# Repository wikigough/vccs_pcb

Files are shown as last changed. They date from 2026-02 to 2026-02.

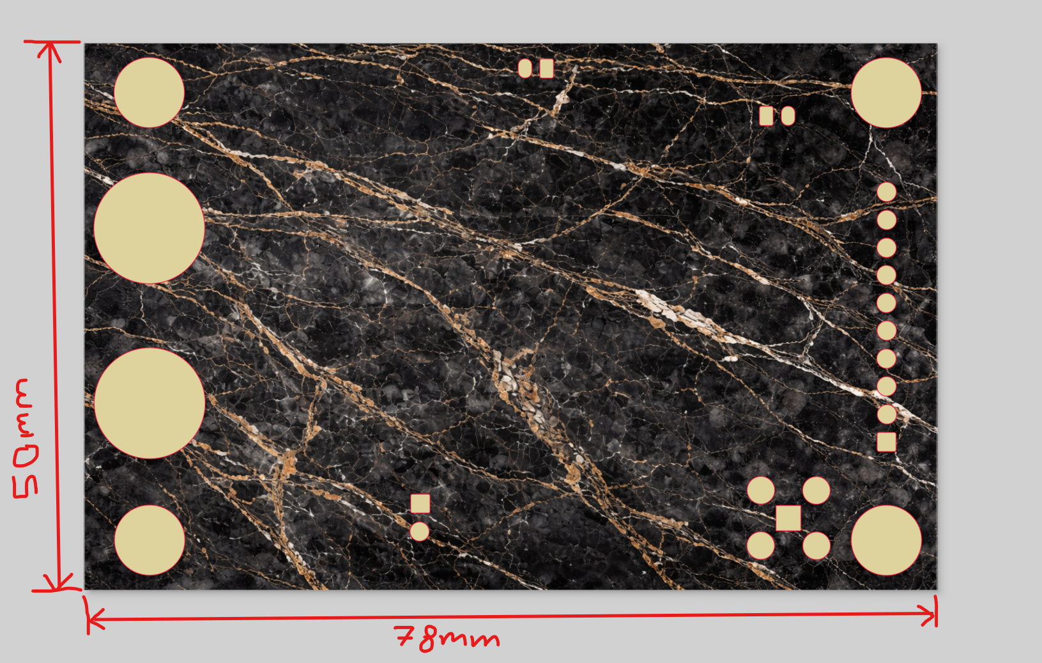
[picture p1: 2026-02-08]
vccs/vccs_release_A1/vccs_art_back_instructions.png

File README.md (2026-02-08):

# Design
## Aims
 - The primary aim of this design was to make a tool for the lab for various testing purposes, which is why there are multiple current modes for the sink.
 - The secondary aim was to experiment with image printing on PCBs and learn how to use Inkscape!

## Design details
The design is a simple voltage controlled current sink. The simulation for the LTSpice circuit simualtion is stored in `\sims`. 
In a nutshell, the sink is controlled by applying 0-1V into the VCONTROL input, either into the SMA connector or the right angled header. 
The `SINK_SELECTx` setting maps the 0-1V voltage input to one of either: 0-3A, 0-1A, 0-100mA, 0-10mA or 0-1mA.
_For inductive loads, please control the slew rate into the VCONTROL input, or adjust the initial passive RC filter from the VCONTROL input, otherwise the control loop may oscillate._

### Image vs silkscreen
 Please note, although there is silkscreen in the KiCAD project, the silkscreen was not generated as a manufacturing output, and was only used as a guide for the image in inkscape. 
 Both silkscreen *and* image printing are allowed, where silkscreen can be applied after the image printing. In hindsight, this combination could've been used.  

### External Control
A right-angled header was put into the design, so that the circuit can be controlled by an external microcontroller. 

## Library
The parts used in the library are stored in a different repo. For passives, the approach of using generic parts and filling them into the schematic was taken. 

# Using the PCBA

## Sink select lines
*One* of the `SINK_SELECTx` lines must be set, either on the board with the onboard DIP switch or by applying voltage on the external header. Please ensure all the DIP switch is all off before plugging in an external controller! Please note that only *one* line is allowed to be set - otherwise you will parallelise sense resistors, unless that is what is wanted.

## Voltage control input
The sink is controlled by inputting a 0-1V voltage waveform into VCONTROL. The voltage can be arbitrary. 

## Fan
For higher power dissipations, a fan must be mounted against the PCB to cool the DPAK transistor, which is the main dissipator of power.

# Data generation and ordering
## Kicad output data generation
Although used PCBWay, used these settings for generating the data output:
https://jlcpcb.com/help/article/how-to-generate-gerber-and-drill-files-in-kicad-9
The size came out as correct in the order page.

## Instructions for ordering
The order screenshots are shown in `\vccs\pcbway_order`.
The png files uploaded are in `\vccs\art\final_images`.
The following guide was used: 
 - https://www.pcbway.com/blog/News/Unlock_Color_PCB_Printing_with_PCBWay_0939d559.html
 - https://www.pcbway.com/project/question/KiCAD_and_Multicolor_Silkscreen.html

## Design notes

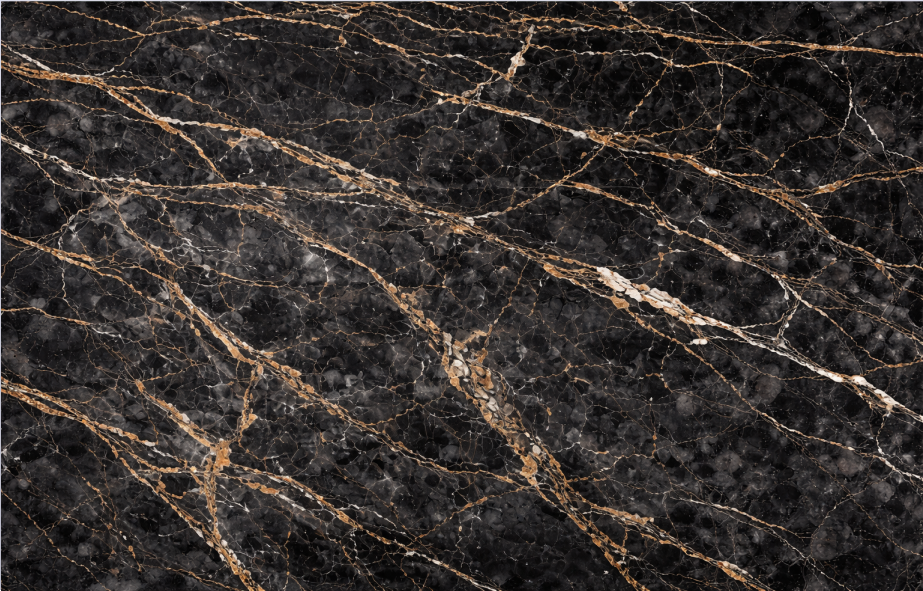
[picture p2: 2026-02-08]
vccs/art/final_images/vccs_art_back.png

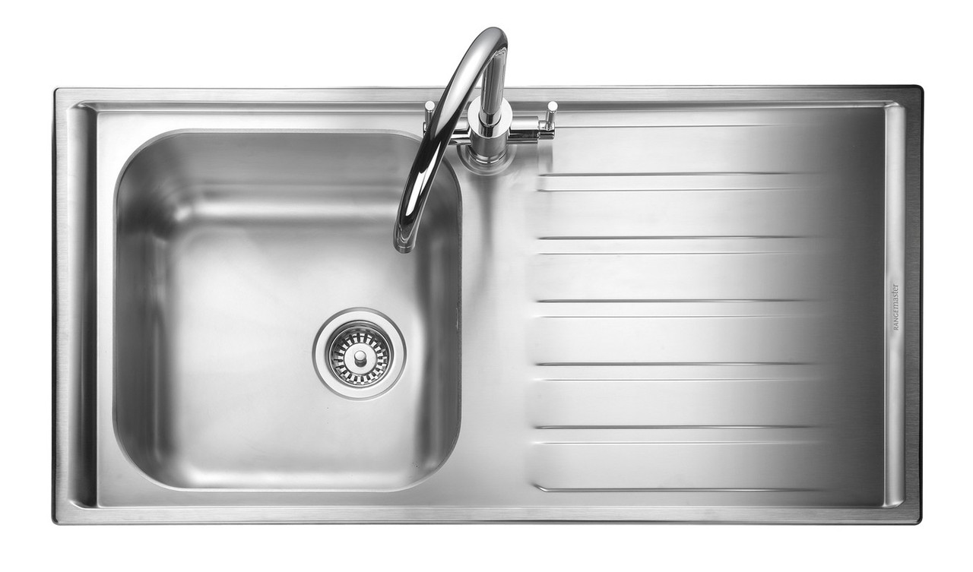
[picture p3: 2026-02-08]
vccs/art/supporting files/another_sink.jpg

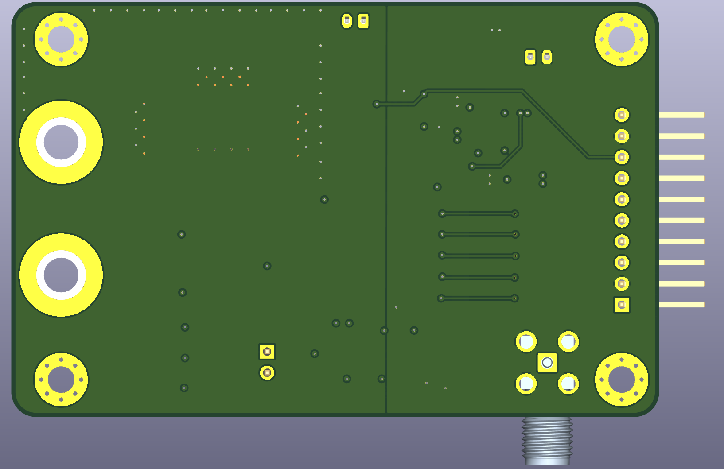
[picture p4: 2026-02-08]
vccs/art/supporting files/back_pcb.png

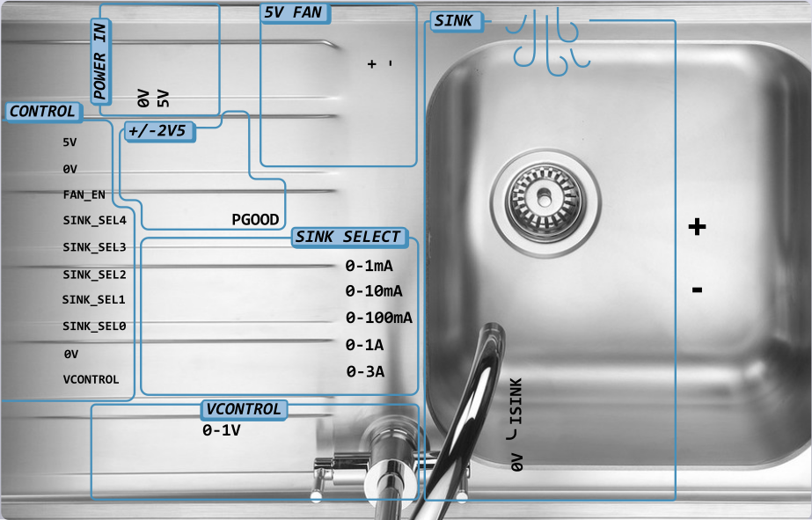
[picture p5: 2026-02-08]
vccs/art/final_images/vccs_art_front.png

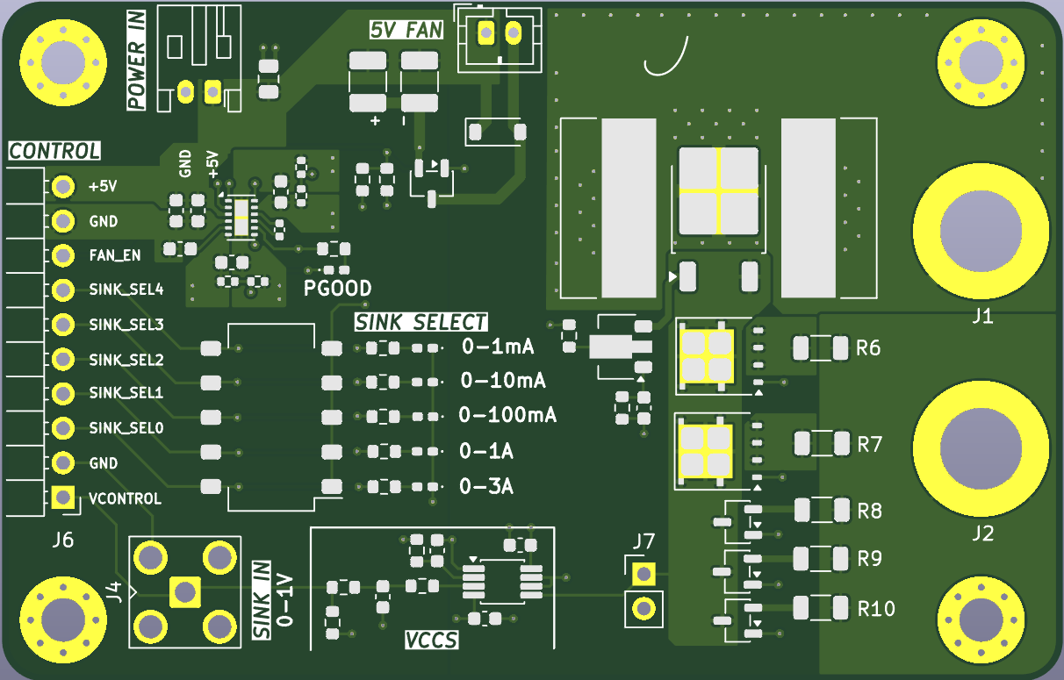
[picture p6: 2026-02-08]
vccs/art/supporting files/front_pcb_bare.png

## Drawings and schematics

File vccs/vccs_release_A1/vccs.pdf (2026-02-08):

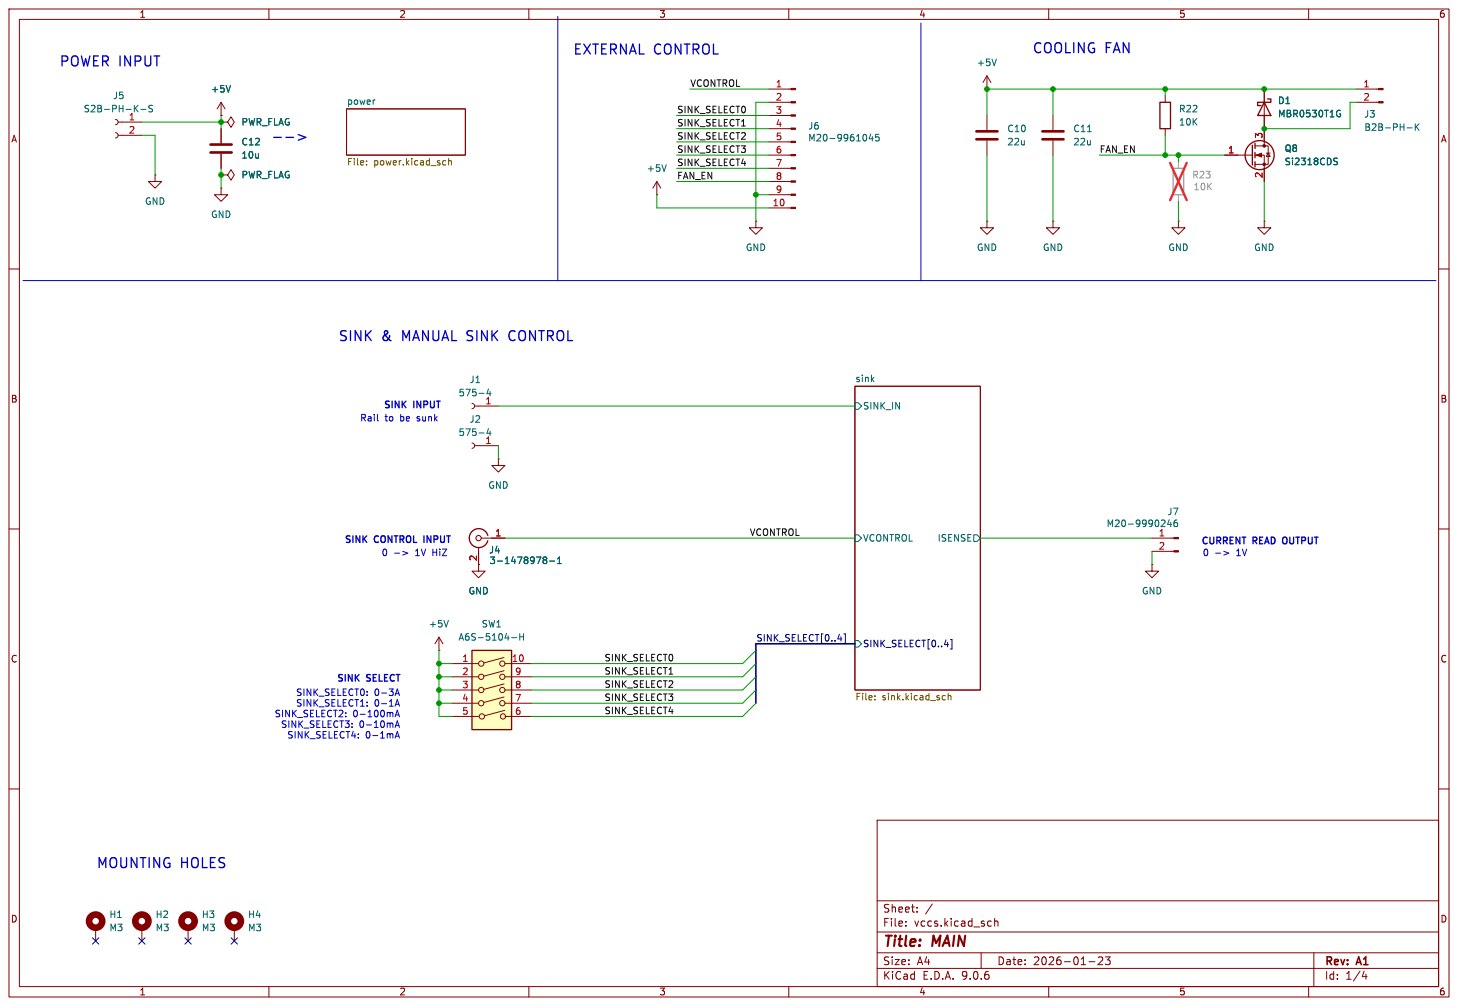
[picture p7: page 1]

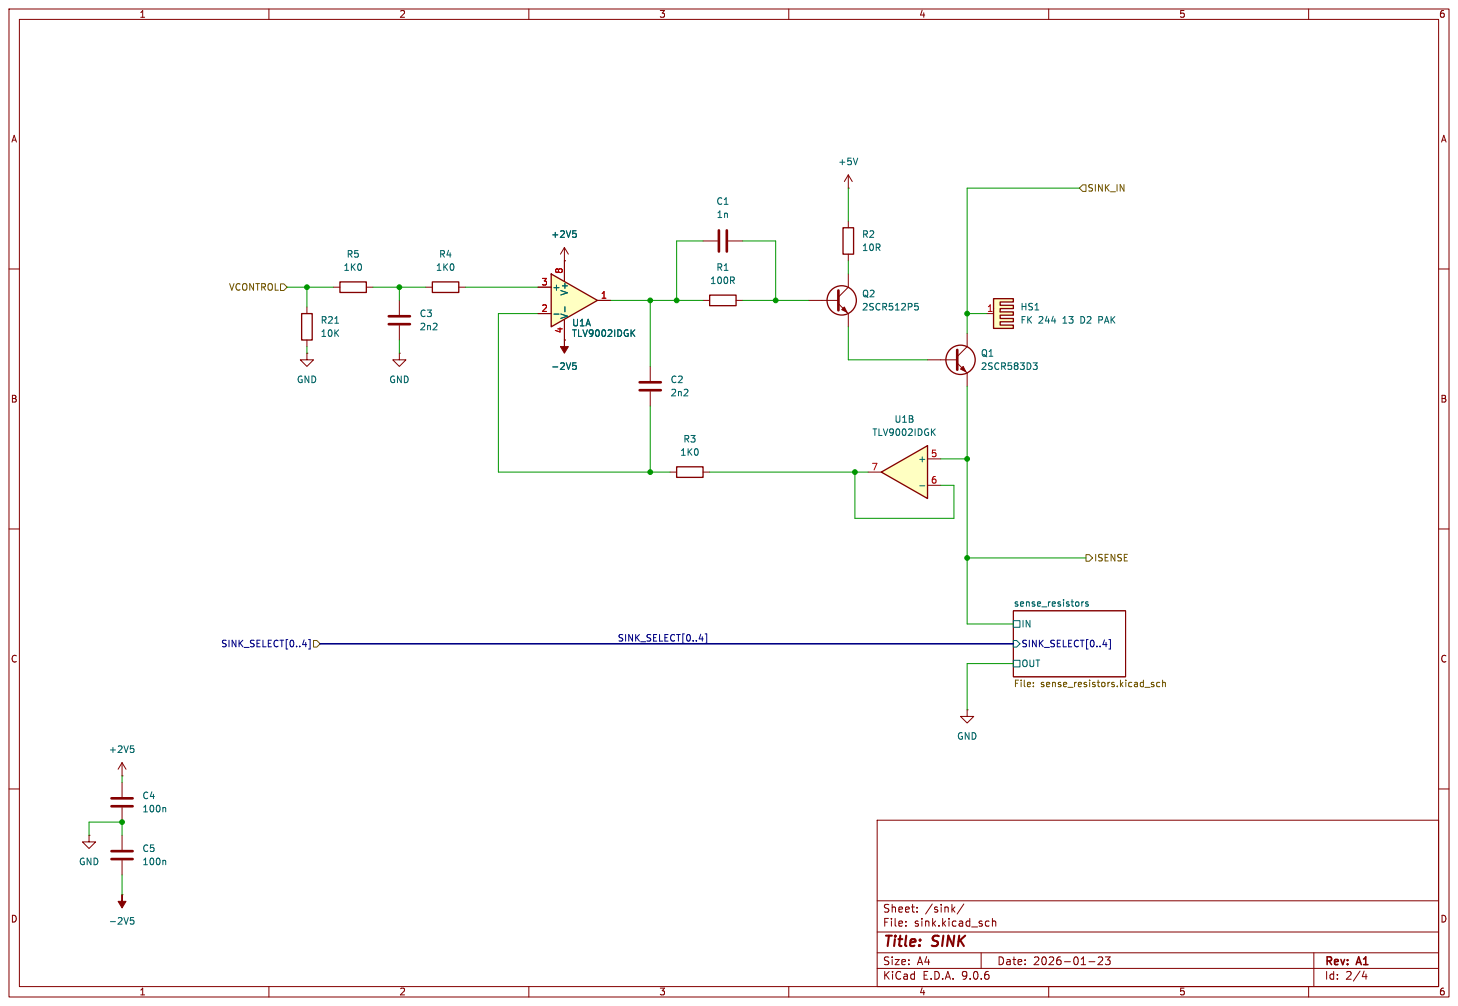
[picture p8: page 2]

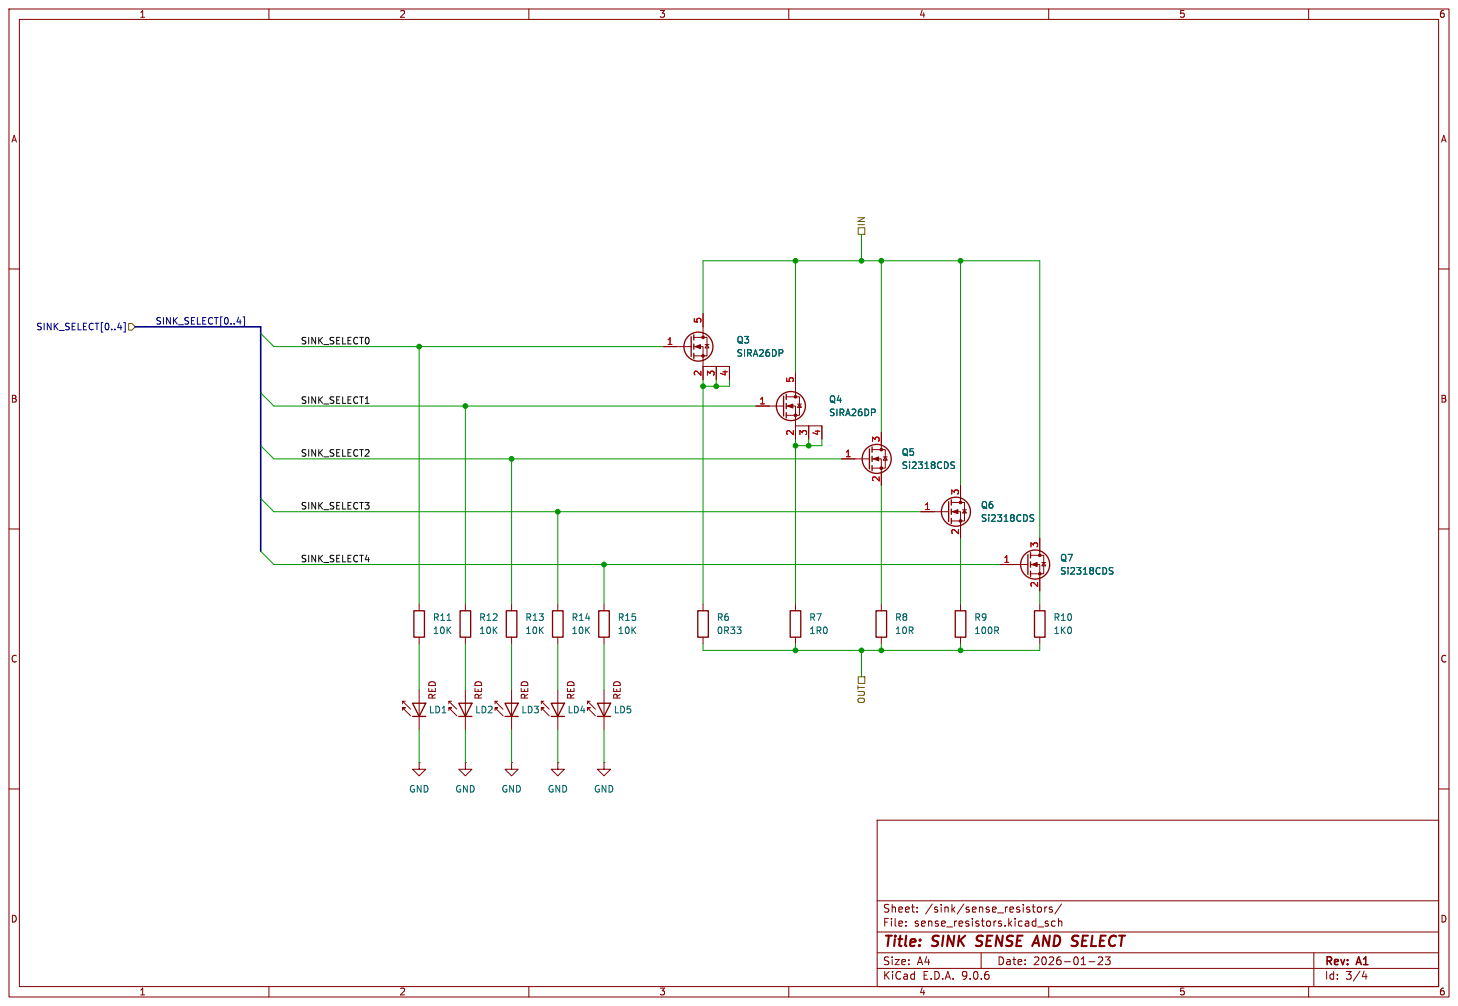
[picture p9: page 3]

Id: 3/4 Title: SINK SENSE AND SELECT

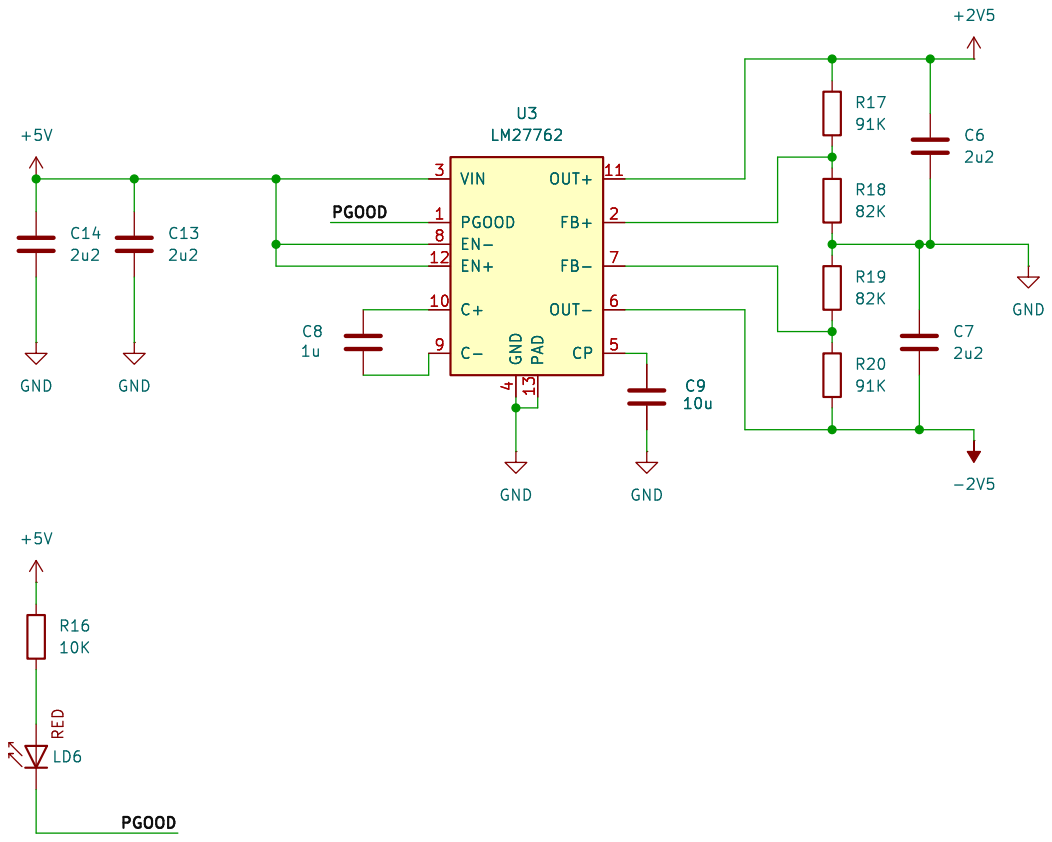
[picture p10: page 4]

4 PAD 13 OUT+ 11 FB+ 2 FB- 7 OUT- 6 CP 5 U3

4 PAD 13 OUT+ 11 FB+ 2 FB- 7 OUT- 6 CP 5 C9

File: power.kicad_sch Sheet: /power/
Id: 4/4 Title: POWER

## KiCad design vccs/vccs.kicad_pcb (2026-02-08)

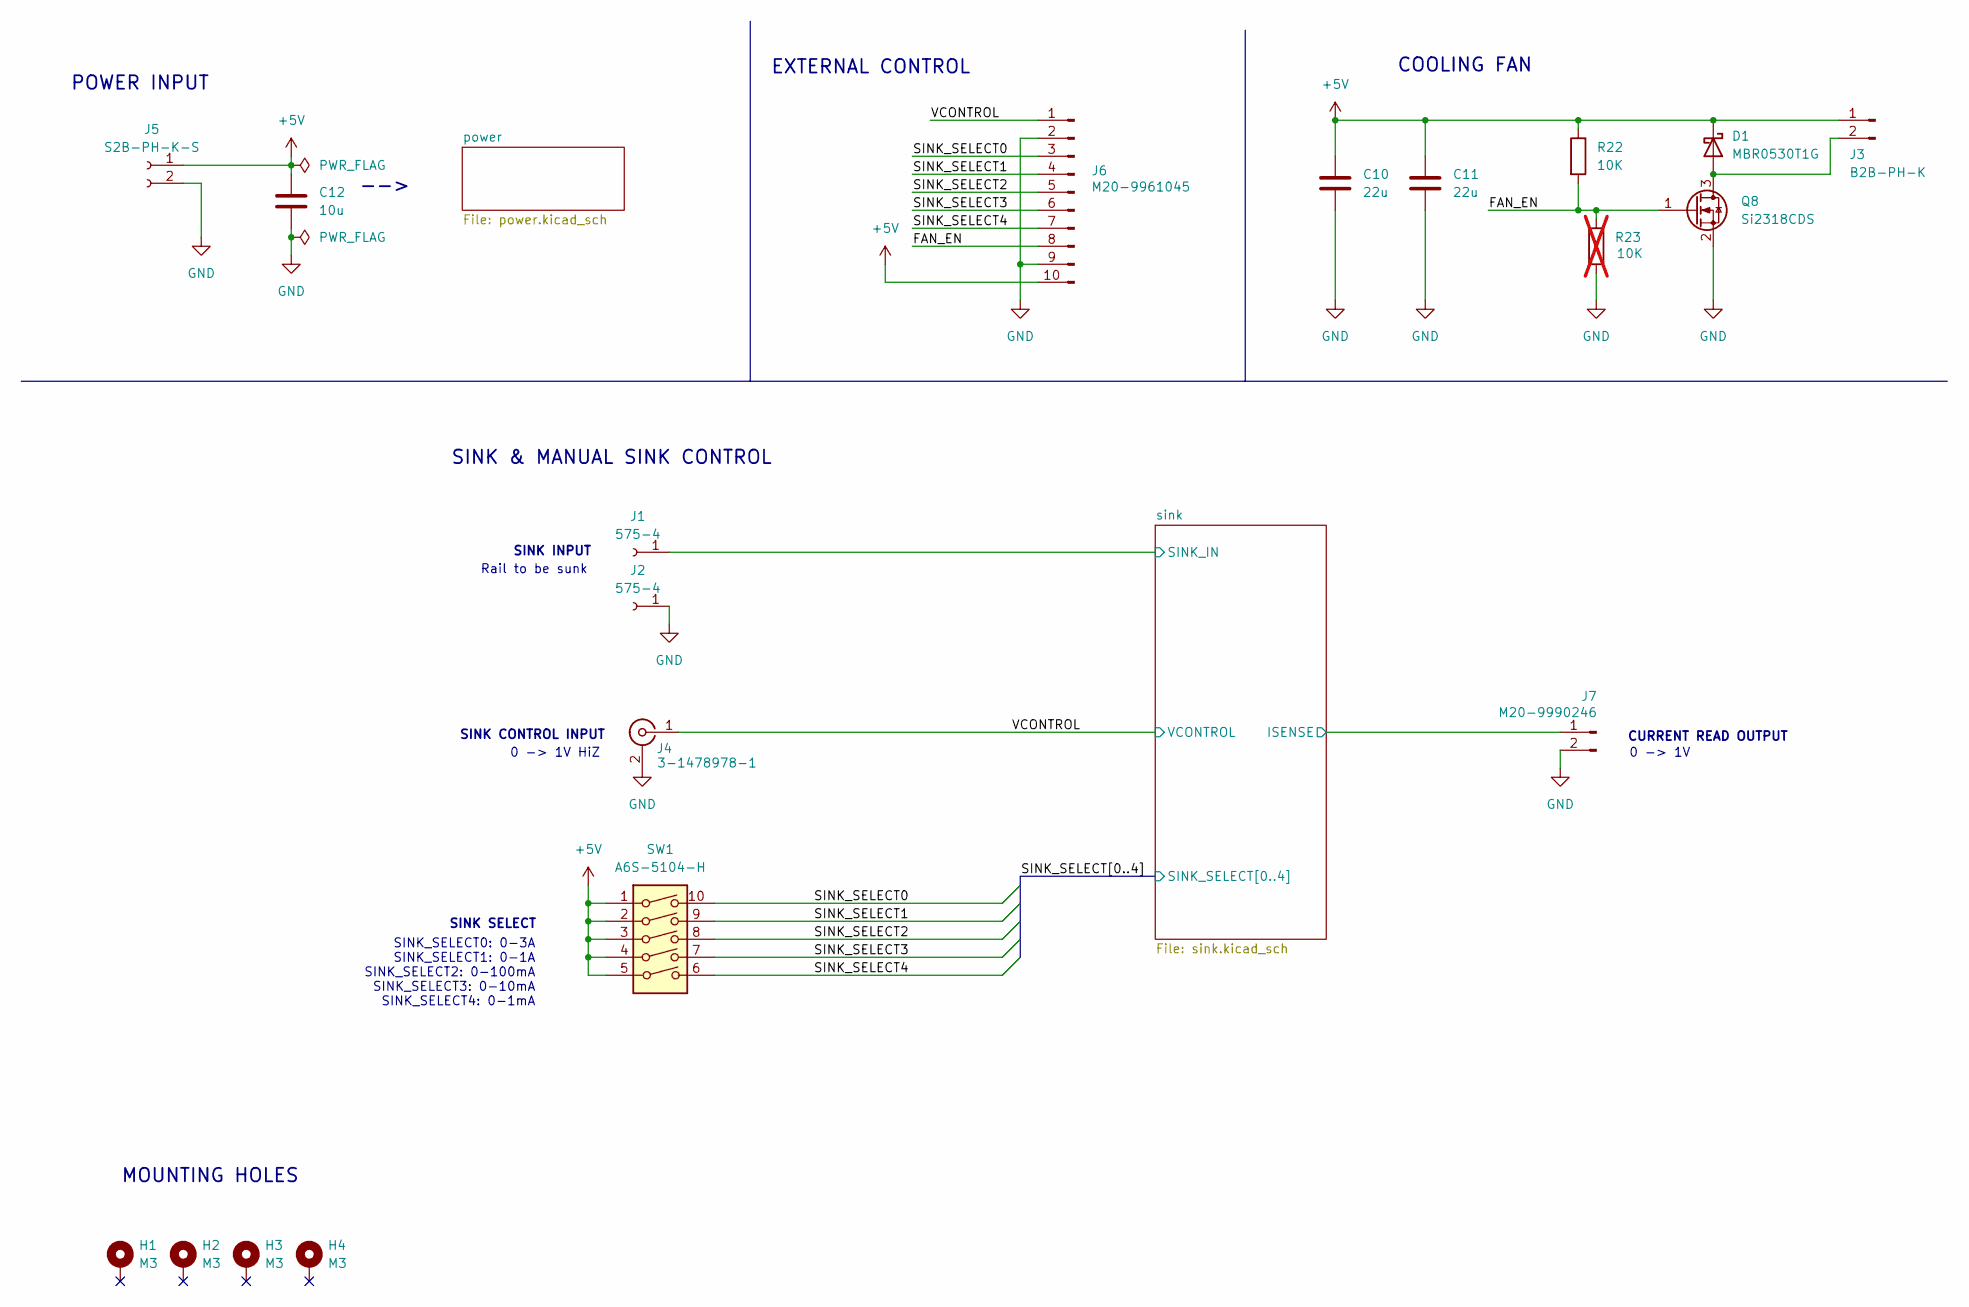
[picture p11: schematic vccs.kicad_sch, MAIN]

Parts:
C10, C11: 22u; C_1210_3225Metric_Pad1.33x2.70mm_HandSolder; Voltage Rating 16V; Tolerance 20%; MPN CL32A226MOJNNNE
C12: 10u; C_0805_2012Metric; Voltage Rating 16V; MPN GRM21BZ71C106KE15L
D1: MBR0530T1G; D_SOD-123; MPN MBR0530T1G
H1, H2, H3, H4: M3; MountingHole_3.2mm_M3_Pad_Via
J1, J2: 575-4; MPN 575-4
J3: B2B-PH-K; JST_PH_B2B-PH-K_1x02_P2.00mm_Vertical; MPN B2B-PH-K
J4: 3-1478978-1; MPN 3-1478978-1
J5: S2B-PH-K-S; JST_PH_S2B-PH-K_1x02_P2.00mm_Horizontal; MPN S2B-PH-K-S
J6: M20-9961045; PinHeader_1x10_P2.54mm_Horizontal; MPN M20-9961045
J7: M20-9990246; PinHeader_1x02_P2.54mm_Vertical; MPN M20-9990246
Q8: Si2318CDS; SOT-23-3; MPN SI2318CDS-T1-BE3
R22: 10K; R_0603_1608Metric; Tolerance 1%; Power Rating 1/10W; MPN RC0603FR-0710KL
R23: 10K; R_0603_1608Metric; Tolerance 1%; Power Rating 1/10W; MPN RC0603FR-0710KL; not fitted
SW1: A6S-5104-H; MPN A6S-5104-H

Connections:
+5V: C10.1, C11.1, C12.1, D1.1 (K), J3.1, J5.1, J6.10, R22.1, SW1.1, SW1.2, SW1.3, SW1.4, SW1.5; also elsewhere on the board
/FAN_EN: J6.8, Q8.1 (G), R22.2, R23.1
/SINK_SELECT0: J6.3, SW1.10; also elsewhere on the board
/SINK_SELECT1: J6.4, SW1.9; also elsewhere on the board
/SINK_SELECT2: J6.5, SW1.8; also elsewhere on the board
/SINK_SELECT3: J6.6, SW1.7; also elsewhere on the board
/SINK_SELECT4: J6.7, SW1.6; also elsewhere on the board
/VCONTROL: J4.1 (In), J6.1; also elsewhere on the board
/sink/ISENSE: J7.1; also elsewhere on the board
/sink/SINK_IN: J1.1; also elsewhere on the board
GND: C10.2, C11.2, C12.2, J2.1, J4.2 (Ext), J5.2, J6.2, J6.9, J7.2, Q8.2 (S), R23.2; also elsewhere on the board
unnamed: D1.2 (A), J3.2, Q8.3 (D)

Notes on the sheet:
Rail to be sunk
0 -> 1V HiZ
-->
SINK & MANUAL SINK CONTROL
0 -> 1V
EXTERNAL CONTROL
COOLING FAN
SINK_SELECT0: 0-3A SINK_SELECT1: 0-1A SINK_SELECT2: 0-100mA SINK_SELECT3: 0-10mA SINK_SELECT4: 0-1mA
CURRENT READ OUTPUT
SINK SELECT
SINK CONTROL INPUT
SINK INPUT
MOUNTING HOLES
POWER INPUT

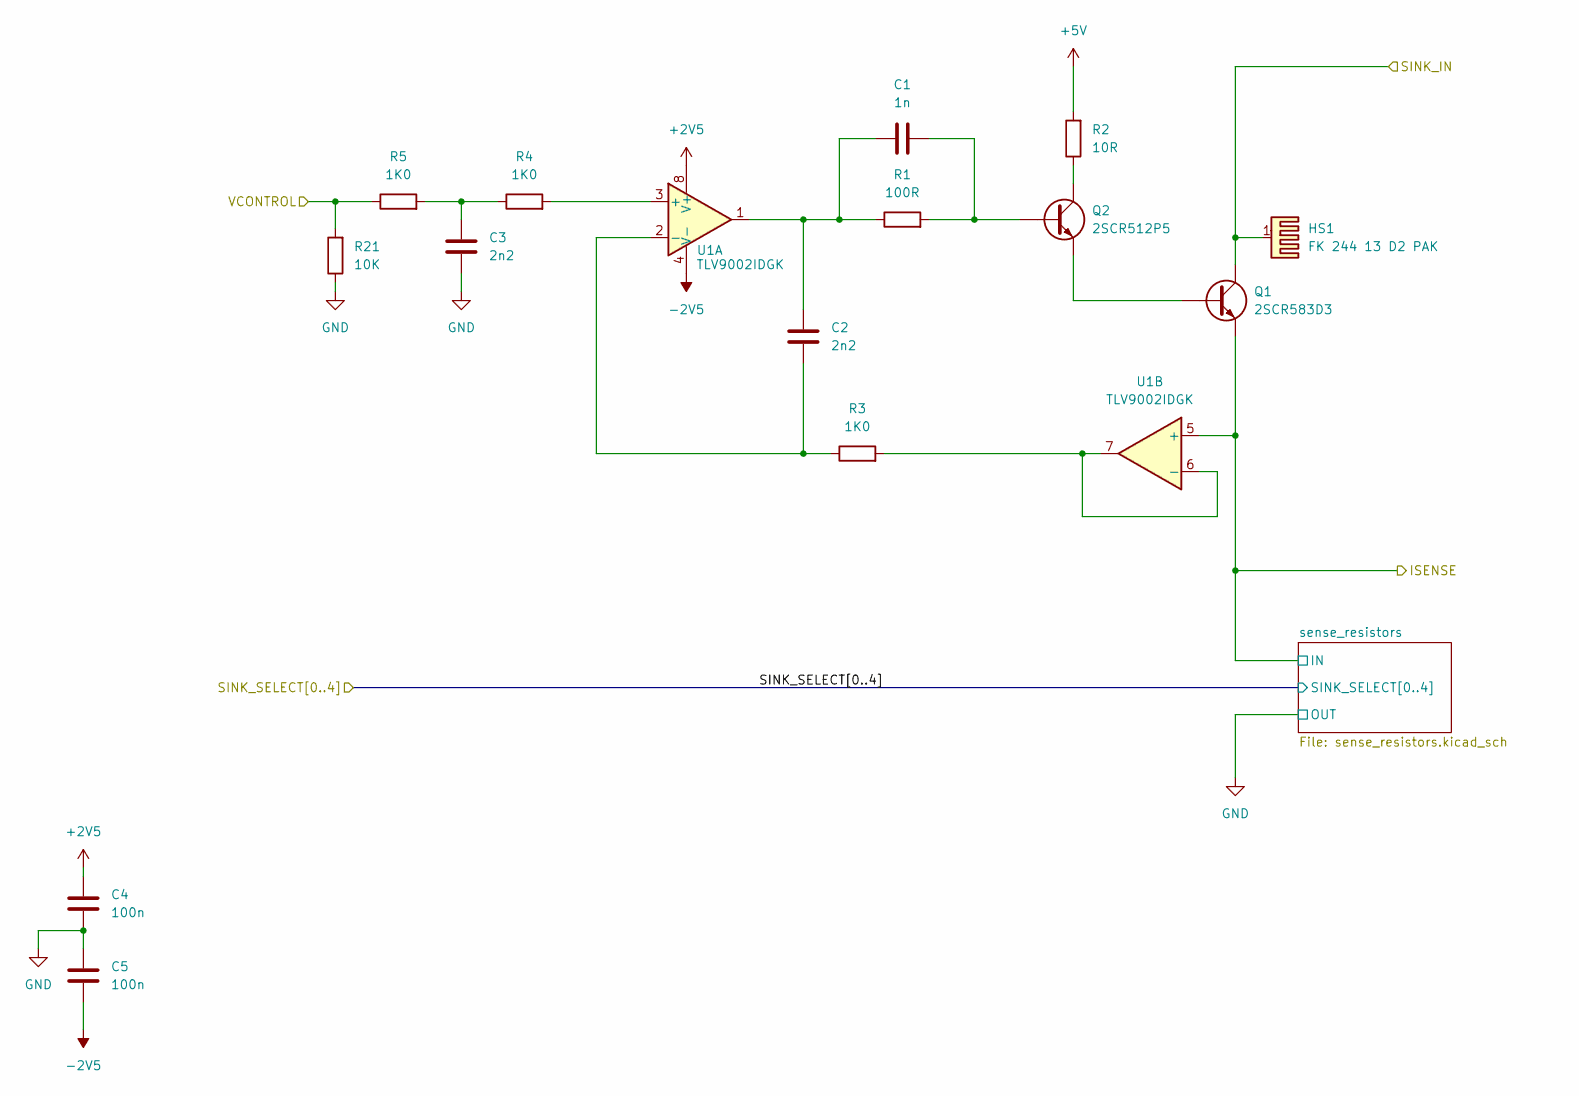
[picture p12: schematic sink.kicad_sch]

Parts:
C1: 1n; C_0603_1608Metric; Voltage Rating 50V; MPN GRM1885C1H102JA01D
C2, C3: 2n2; C_0603_1608Metric; Voltage Rating 50V; MPN GRM1885C1H222JA01D
C4, C5: 100n; C_0603_1608Metric; Voltage Rating 50V; MPN GCJ188R71H104KA12D
HS1: FK 244 13 D2 PAK; MPN FK 244 13 D2 PAK
Q1: 2SCR583D3; TO-252-2; MPN 2SCR583D3
Q2: 2SCR512P5; SOT-89-3; MPN 2SCR512P5
R1: 100R; R_0603_1608Metric; Tolerance 1%; Power Rating 1/10W; MPN RC0603FR-07100RL
R2: 10R; R_0603_1608Metric; Tolerance 1%; Power Rating 1/10W; MPN RC0603FR-0710RL
R3, R4, R5: 1K0; R_0603_1608Metric; Tolerance 1%; Power Rating 1/10W; MPN RC0603FR-071KL
R21: 10K; R_0603_1608Metric; Tolerance 1%; Power Rating 1/10W; MPN RC0603FR-0710KL
U1: TLV9002IDGK; VSSOP-8_3x3mm_P0.65mm; MPN TLV9002IDGK

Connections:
+2V5: C4.2, U1.8 (V+); also elsewhere on the board
+5V: R2.2; also elsewhere on the board
-2V5: C5.1, U1.4 (V-); also elsewhere on the board
/VCONTROL: R5.1, R21.2; also elsewhere on the board
/sink/ISENSE: Q1.3 (E), U1.5 (+); also elsewhere on the board
/sink/SINK_IN: HS1.1, Q1.2 (C); also elsewhere on the board
GND: C3.1, C4.1, C5.2, R21.1; also elsewhere on the board
unnamed: C1.1, C2.2, R1.1, U1.1
unnamed: C3.2, R4.1, R5.2
unnamed: Q1.1 (B), Q2.3 (E)
unnamed: C1.2, Q2.1 (B), R1.2
unnamed: Q2.2 (C), R2.1
unnamed: R4.2, U1.3 (+)
unnamed: C2.1, R3.1, U1.2 (-)
unnamed: R3.2, U1.6 (-), U1.7

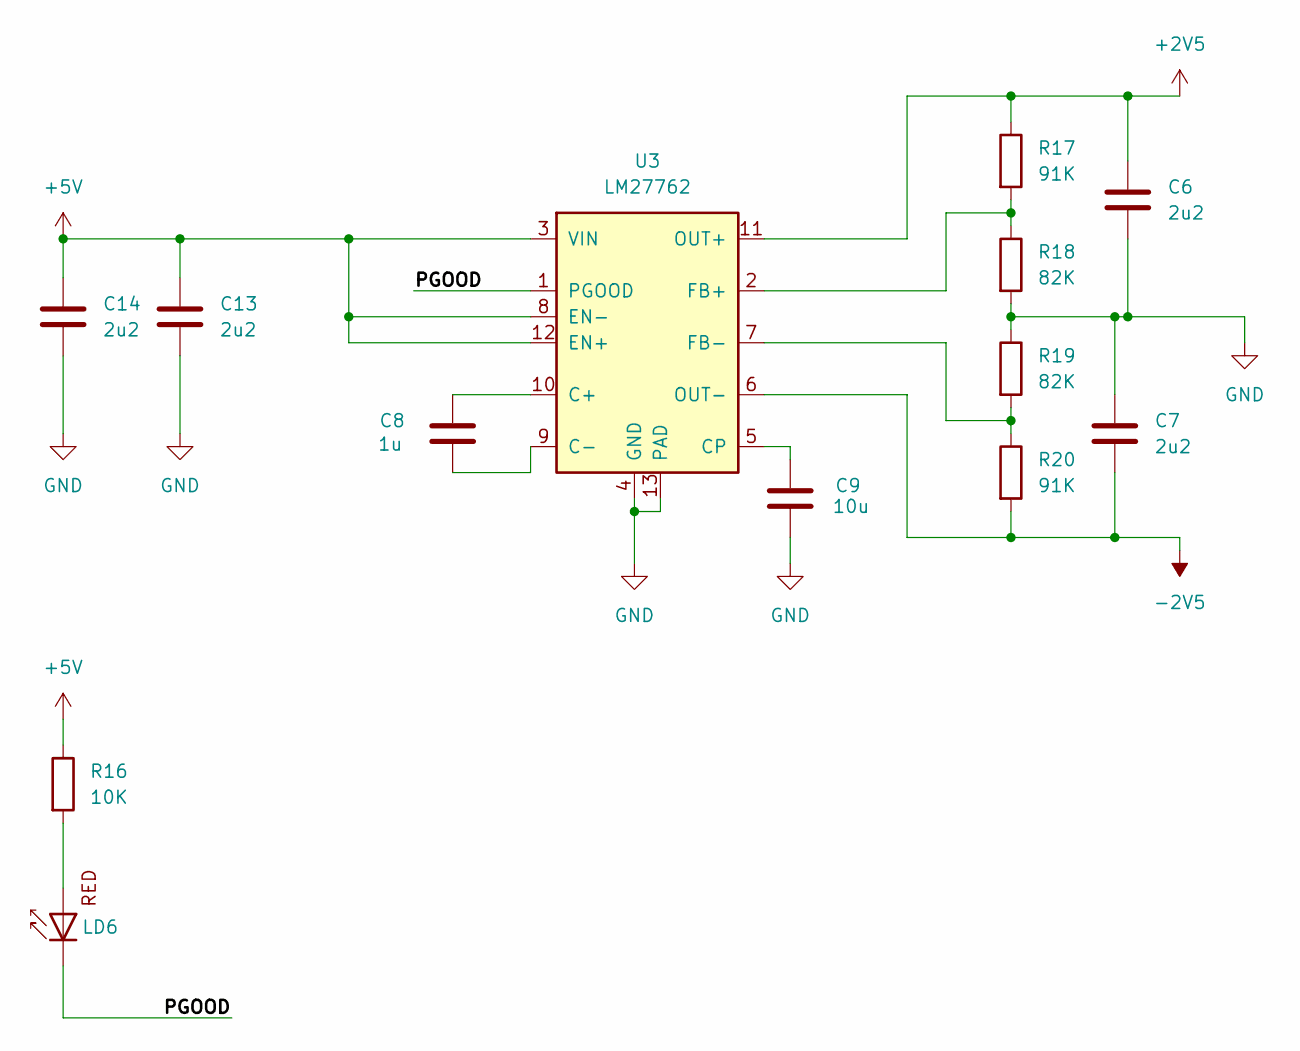
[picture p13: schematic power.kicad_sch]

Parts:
C6, C7, C13, C14: 2u2; C_0603_1608Metric; Voltage Rating 16V; MPN GRM188Z71C225KE43D
C8: 1u; C_0402_1005Metric; Voltage Rating 16V; MPN GRM155R61C105KA12D
C9: 10u; C_0603_1608Metric; Voltage Rating 16V; MPN GRM188R61C106MAALD
LD6: APHHS1005LSECK/J3-PF; LED_0402_1005Metric_Pad0.77x0.64mm_HandSolder; MPN APHHS1005LSECK/J3-PF
R16: 10K; R_0603_1608Metric; Tolerance 1%; Power Rating 1/10W; MPN RC0603FR-0710KL
R17, R20: 91K; R_0402_1005Metric; Tolerance 1%; Power Rating 1/16W; MPN RC0402FR-0791KL
R18, R19: 82K; R_0402_1005Metric; Tolerance 1%; Power Rating 1/16W; MPN RC0402FR-0782KL
U3: LM27762; WSON-12-1EP_3x2mm_P0.5mm_EP1x2.65; MPN LM27762DSS

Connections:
+2V5: C6.1, R17.1, U3.11 (OUT+); also elsewhere on the board
+5V: C13.1, C14.1, R16.1, U3.3 (VIN), U3.8 (EN-), U3.12 (EN+); also elsewhere on the board
-2V5: C7.2, R20.2, U3.6 (OUT-); also elsewhere on the board
/power/PGOOD: LD6.1 (K), U3.1 (PGOOD)
GND: C6.2, C7.1, C9.1, C13.2, C14.2, R18.2, R19.1, U3.4 (GND), U3.13 (PAD); also elsewhere on the board
unnamed: LD6.2 (A), R16.2
unnamed: C8.1, U3.10 (C+)
unnamed: C8.2, U3.9 (C-)
unnamed: C9.2, U3.5 (CP)
unnamed: R17.2, R18.1, U3.2 (FB+)
unnamed: R19.2, R20.1, U3.7 (FB-)

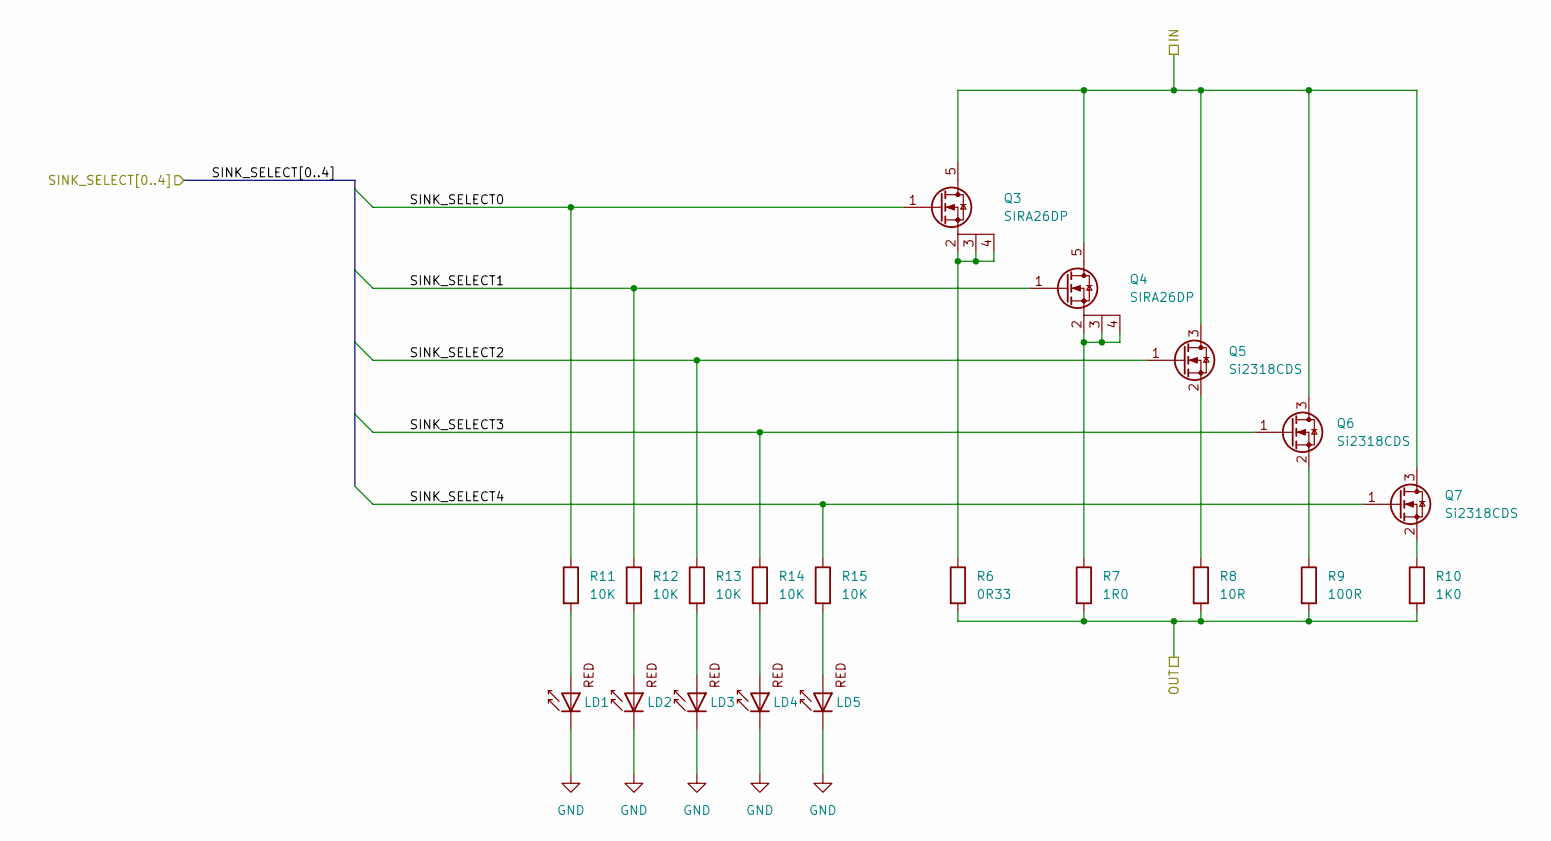
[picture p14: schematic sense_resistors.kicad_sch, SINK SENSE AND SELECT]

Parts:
LD1, LD2, LD3, LD4, LD5: APHHS1005LSECK/J3-PF; LED_0402_1005Metric_Pad0.77x0.64mm_HandSolder; MPN APHHS1005LSECK/J3-PF
Q3, Q4: SIRA26DP; PowerPAK_SO-8L_Single; MPN SIRA26DP-T1-RE3
Q5, Q6, Q7: Si2318CDS; SOT-23-3; MPN SI2318CDS-T1-BE3
R6: 0R33; R_1206_3216Metric; Tolerance 1%; Power Rating 1/4W; MPN RL1206FR-070R33L
R7: 1R0; R_1206_3216Metric; Tolerance 1%; Power Rating 1/4W; MPN RC1206FR-131RL
R8: 10R; R_1206_3216Metric; Tolerance 1%; Power Rating 1/4W; MPN RC1206FR-0710RL
R9: 100R; R_1206_3216Metric; Tolerance 1%; Power Rating 1/4W; MPN RC1206FR-07100RL
R10: 1K0; R_1206_3216Metric; Tolerance 1%; Power Rating 1/4W; MPN RC1206FR-071KL
R11, R12, R13, R14, R15: 10K; R_0603_1608Metric; Tolerance 1%; Power Rating 1/10W; MPN RC0603FR-0710KL

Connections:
/SINK_SELECT0: Q3.1 (G), R11.1; also elsewhere on the board
/SINK_SELECT1: Q4.1 (G), R12.1; also elsewhere on the board
/SINK_SELECT2: Q5.1 (G), R13.1; also elsewhere on the board
/SINK_SELECT3: Q6.1 (G), R14.1; also elsewhere on the board
/SINK_SELECT4: Q7.1 (G), R15.1; also elsewhere on the board
/sink/ISENSE: Q3.5 (D), Q4.5 (D), Q5.3 (D), Q6.3 (D), Q7.3 (D); also elsewhere on the board
GND: LD1.1 (K), LD2.1 (K), LD3.1 (K), LD4.1 (K), LD5.1 (K), R6.2, R7.2, R8.2, R9.2, R10.2; also elsewhere on the board
unnamed: LD1.2 (A), R11.2
unnamed: LD2.2 (A), R12.2
unnamed: LD3.2 (A), R13.2
unnamed: LD4.2 (A), R14.2
unnamed: LD5.2 (A), R15.2
unnamed: Q3.2 (S), Q3.3 (S), Q3.4 (S), R6.1
unnamed: Q4.2 (S), Q4.3 (S), Q4.4 (S), R7.1
unnamed: Q5.2 (S), R8.1
unnamed: Q6.2 (S), R9.1
unnamed: Q7.2 (S), R10.1

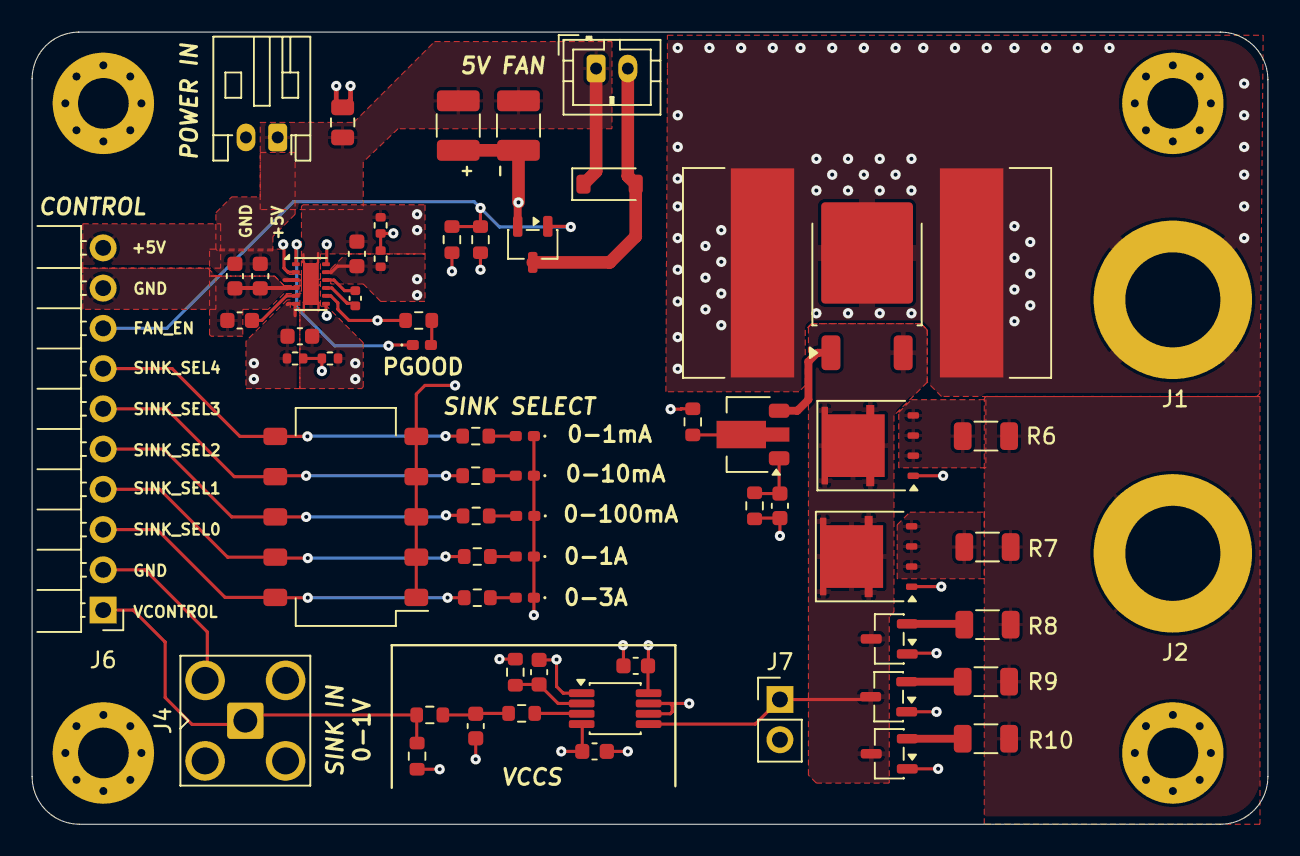
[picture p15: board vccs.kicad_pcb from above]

Board: 4 copper layers, 78.0 x 50.0 mm, 67 parts (0 on the bottom side), 39 nets.

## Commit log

2026-01-18 first initial commit
    Added .gitignore for KiCad and LTSpice and added empty project files.
    [vccs.kicad_pcb, vccs.kicad_sch]
2026-01-18 Iterated sim and now putting into KiCad
    [power.kicad_sch, sense_resistors.kicad_sch, sink.kicad_sch, vccs.kicad_sch]
2026-02-07 DRC pass
    Check in before adding artwork and double checking parts.
    [power.kicad_sch, sense_resistors.kicad_sch, sink.kicad_sch, vccs.kicad_pcb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]
2026-02-08 A1 RELEASE
    A1 released - pending feedback from PCBWay
    [power.kicad_sch, sense_resistors.kicad_sch, sink.kicad_sch, vccs-B_Cu.gbr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]
